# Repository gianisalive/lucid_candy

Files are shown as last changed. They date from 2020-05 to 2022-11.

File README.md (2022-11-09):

# Lucid Candy
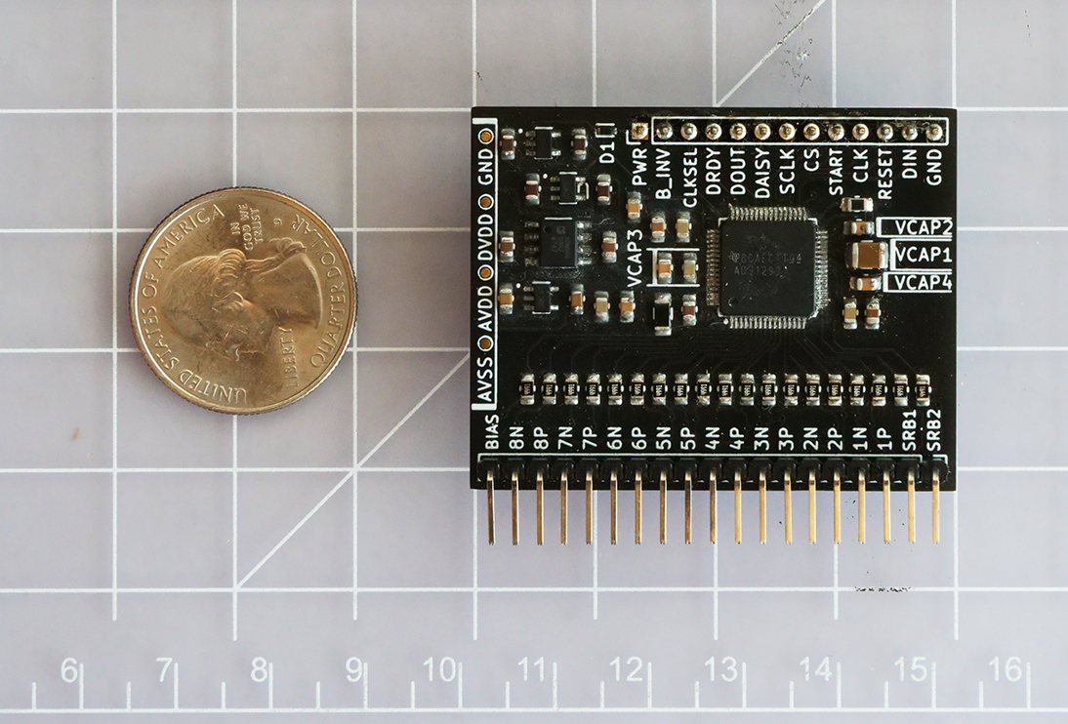
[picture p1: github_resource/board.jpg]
board pic

A bare minimum 8 channel EEG board with TI ads1299 chip. It can be driven with any microcontroller that has 3.3V logic. Multiple boards can be chained together to record with 16 or 24 channels. This repository includes KiCad files and SPI example.

## Disclaimer
It still needs a lot of improvement, professional guidance and review. In no way it's fully tested to perform under clinical setting. Please use basic principles to test and evaluate before using it. All suggestions are highly appreciated: gianisalive@gmail.com

## Who should use it?
No one really should, but if you're a newbie in electronics, software, and neuroscience, and want to learn more by building, then this might be a thing for you. If you're just looking for an affordable EEG, there're better open source ones out there, such as [OpenBCI](https://openbci.com/).

## Files & Locations
|-- lucid_candy  
|---- component_datasheet------important datasheet of the components used for the board  
|---- e_component---------------all the KiCad pcb footprint (from SnapEDA) for the components  
|---- eeg------------------------KiCad design files  
|---- firmware-------------------example of Arduino DUE communicating with the board via SPI  
|---- gerber_zip-----------------same file used to produce the current board with JLCPCB  

## Schematics
The philosophy with current version of the design is to work within TI's recommendation, and choose components with least amount of tolerance/inductance to develope a baseline. In the future, any design improvement can be evaluated/compared to the current design.
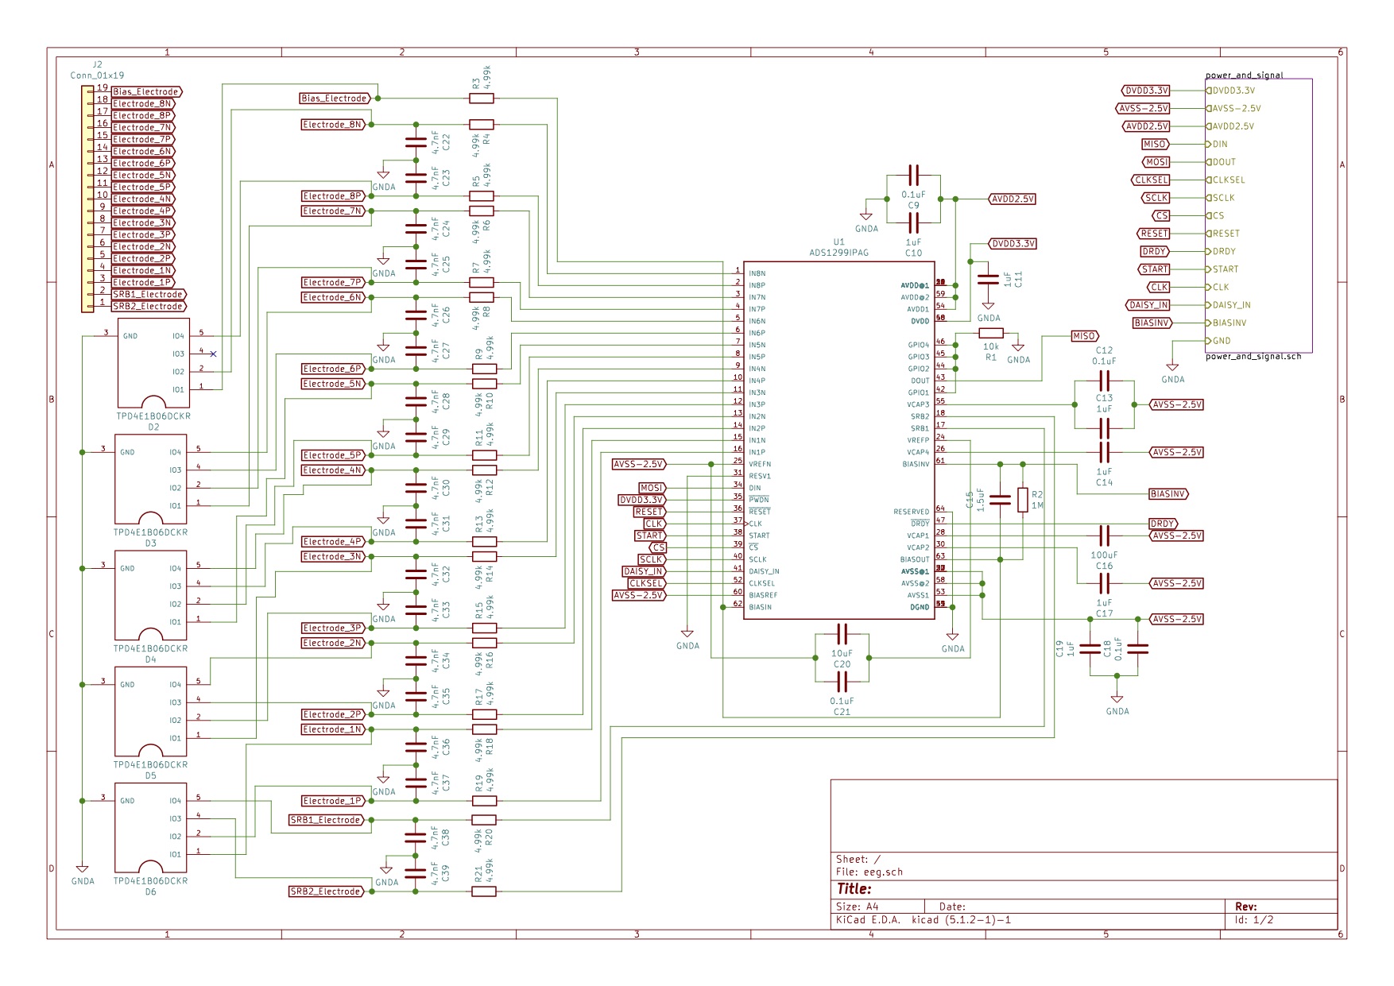
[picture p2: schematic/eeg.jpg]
eeg_schematics

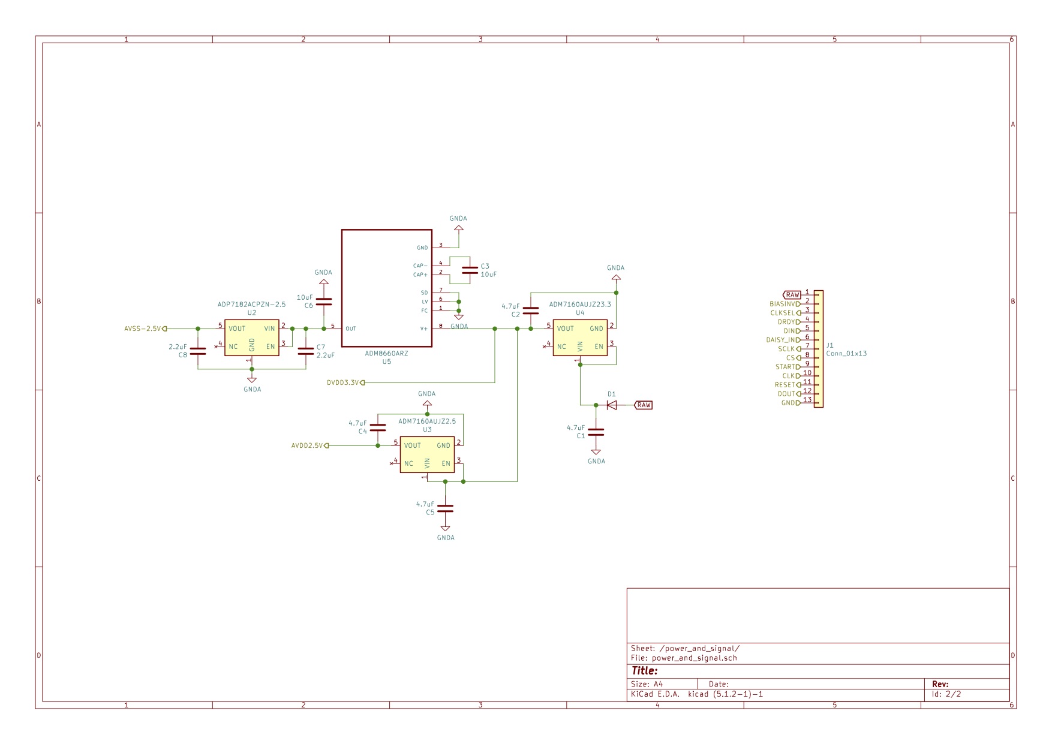
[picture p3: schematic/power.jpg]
power_schematics


## Components
All the component used can be found [here](https://docs.google.com/spreadsheets/d/1N4UGuHjUGolRgQoIL3MemhwEijfZmJlSR52b1LrSyF4/edit?usp=sharing). Some of these are pretty over priced. In most situations, you can probably get away with cheaper parts.

## Programming in a nutshell
**Overview:**  
- Data are transfered via SPI MODE1 with MSB first
- Data are retrieve with no-op command 0x00
- Chip has an internal clock. If BYOO (bring your own oscillator), then connect it to CLK pin, and tie CLKSEL low.  

**Power up sequence:**  
- Set CLKSEL pin high to enable internal oscillator
- Set RESET pin high, and make sure VCAP1 is settled around 1.1V
- Send reset command, and at this point DRDY pin should toggle at around 250Hz
- Send SDATAC (stop data continuous) command
- Set CONFIG1(0x01), CONFIG2(0x02) and CONFIG3(0x03)
- Set CHnSET (single ended, double ended or generate test signal)

**Data conversion:**  
- After sending RDATA or RDATAC command, data is returned on the second rising edge of the DRDY pin
- Initial 3 bytes are status data, and it always starts with 1100. Then it'll transfer 3 bytes of data per channel. An 8 channel board will have 8 * 3 + 3 = 27 bytes of data
- Data are structured in 2's compliment. The MSB is used to determin whether the value is positive or negative
- V = LSB * (2 * 4.5 / 24) / (2 ^ 24) // LSB = decimal value of 3 bytes channel data

## Testing
Fully assembled device with current Arduino firmware is tested with a calibrated Keysight DSOX1204G oscilloscope/function generator.

## Chanllenges
In a nutshell, eliminating noises and extracting the signal is one of the most chanllenging part when it comes to designing the hardware and the software.  
Neurons communcate via electrical signals (Action Potentials). When neurons are ready to send signals to neighboring neurons, they produce about 100 mV spike in less than 3 ms. These signals are further attenuated (reduction in signal strength) by the surrounding anatomical structures. When the electrode receives the signal, it's been attenuated to uV scale. In order to extract the signals, we need to filter out the noise with minimal distortion to the signal. There're few methods suggest that're yet to be implemented, such as bandpass filter, CleanLine and infinite impulse response.

## Miscellaneous
Some silly questions I asked:
 - [voltage offset](https://e2e.ti.com/support/data-converters/f/73/p/912858/3374371#3374371)

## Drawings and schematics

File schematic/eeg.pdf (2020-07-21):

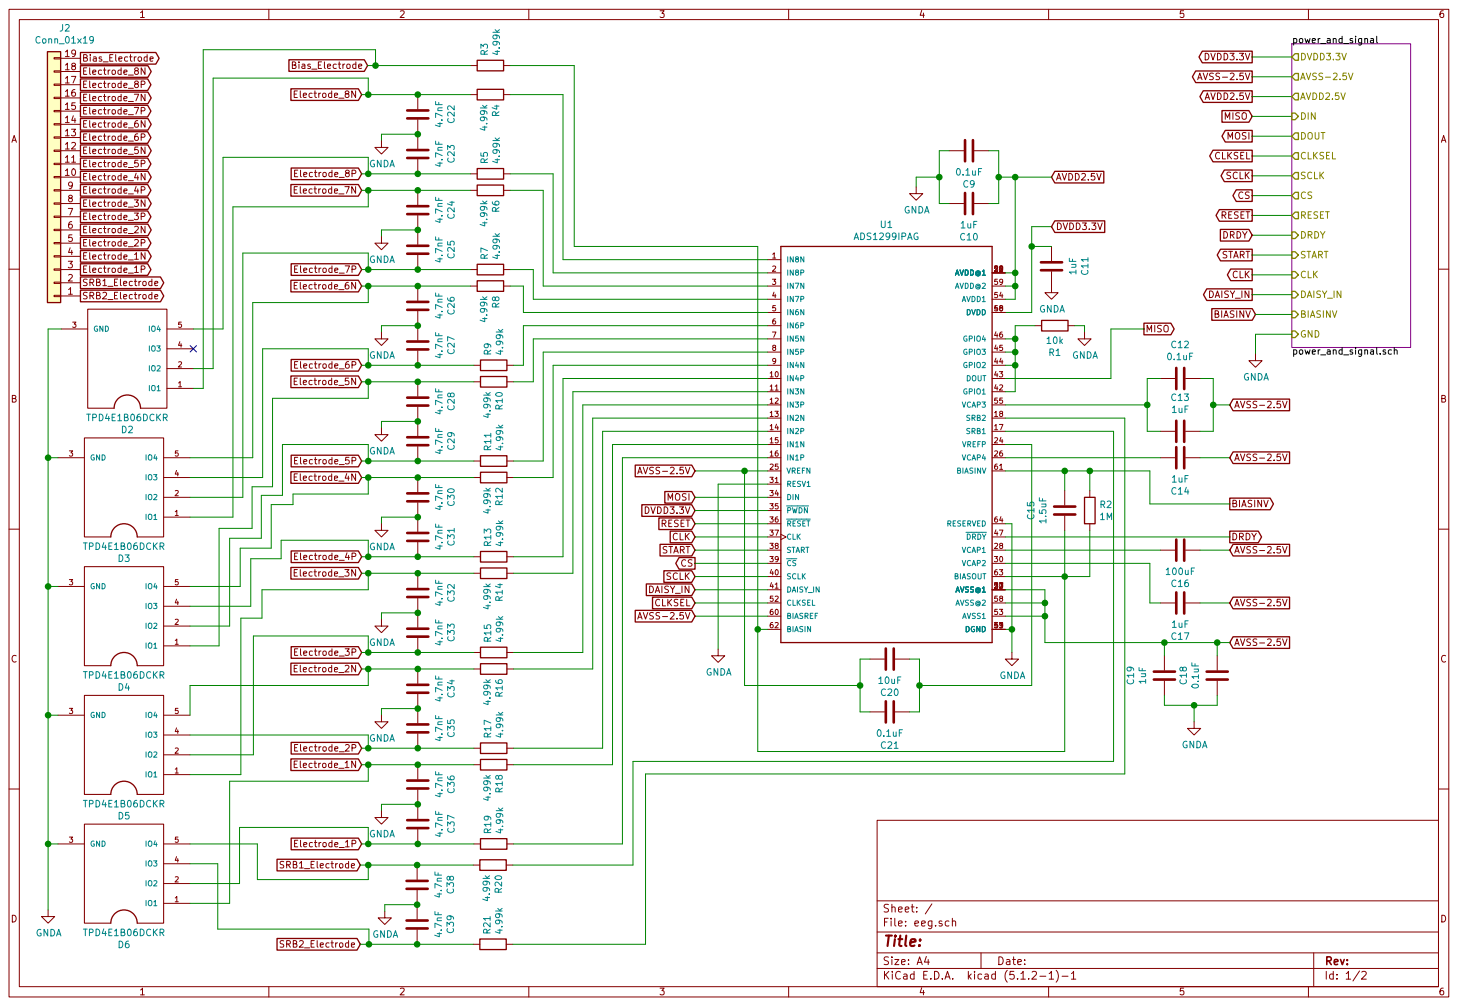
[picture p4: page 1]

IN5N 7
IN5P 8
IN4N 9
IN4P 10
IN3N 11
IN3P 12
IN2N 13

File: eeg.sch Sheet: /

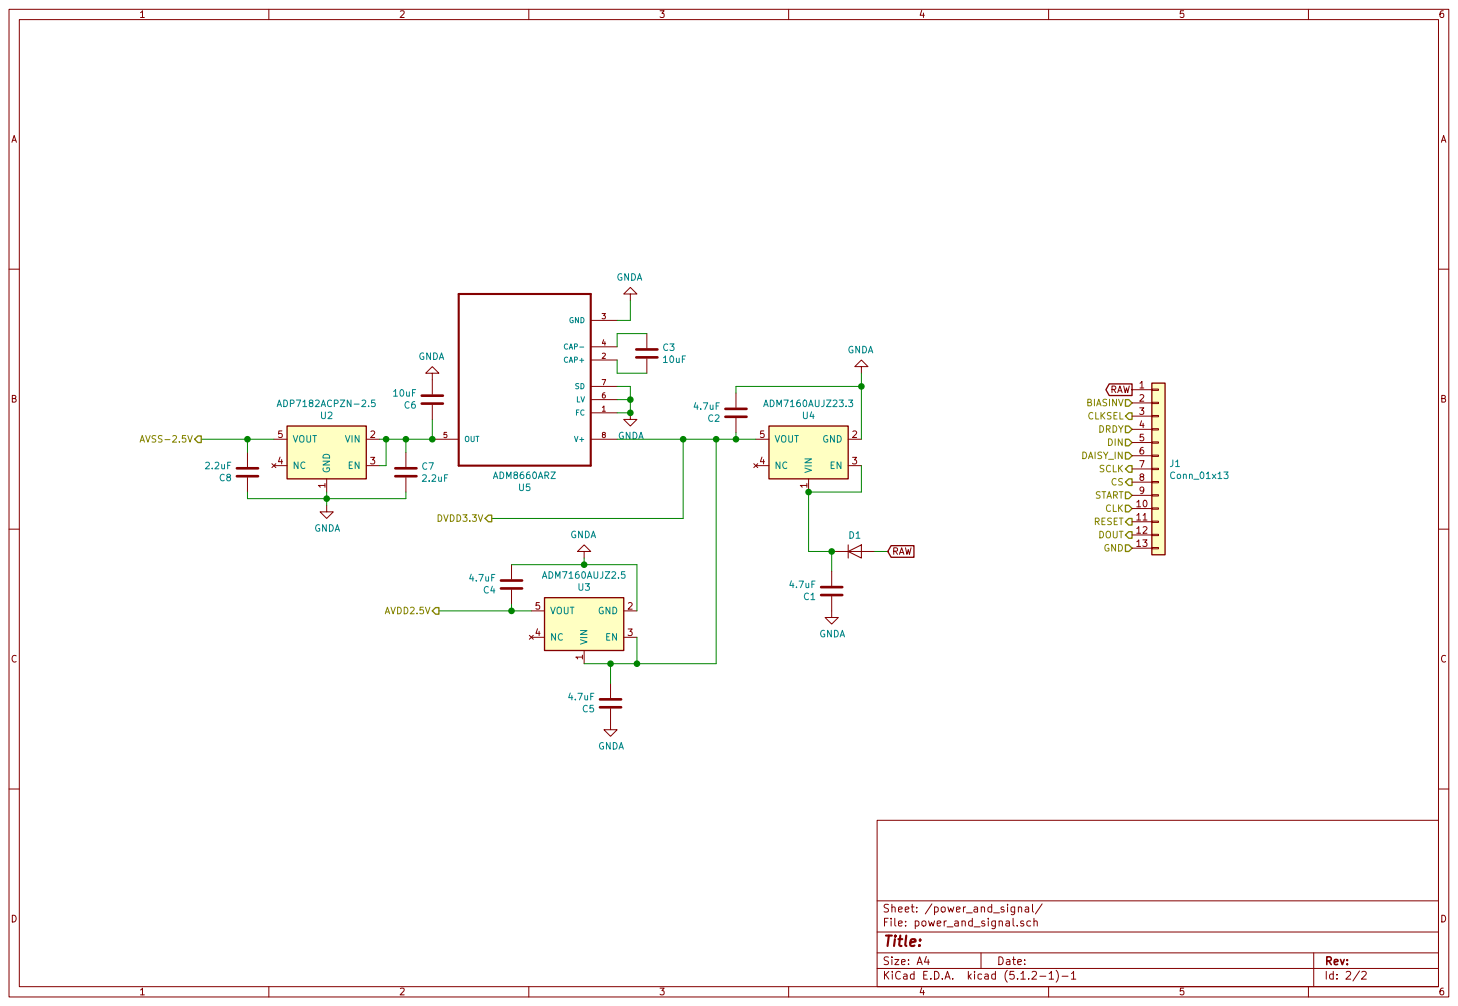
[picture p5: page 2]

1 VIN 2 EN 3 NC 4 VOUT 5 U2 ADP7182ACPZN-2.5 GNDA C7 C8 2.2uF

1 GND 2 EN 3 NC 4 VOUT 5 U4 ADM7160AUJZ23.3 C2

1 GND 2 EN 3 NC 4 VOUT 5 U3 ADM7160AUJZ2.5 C4

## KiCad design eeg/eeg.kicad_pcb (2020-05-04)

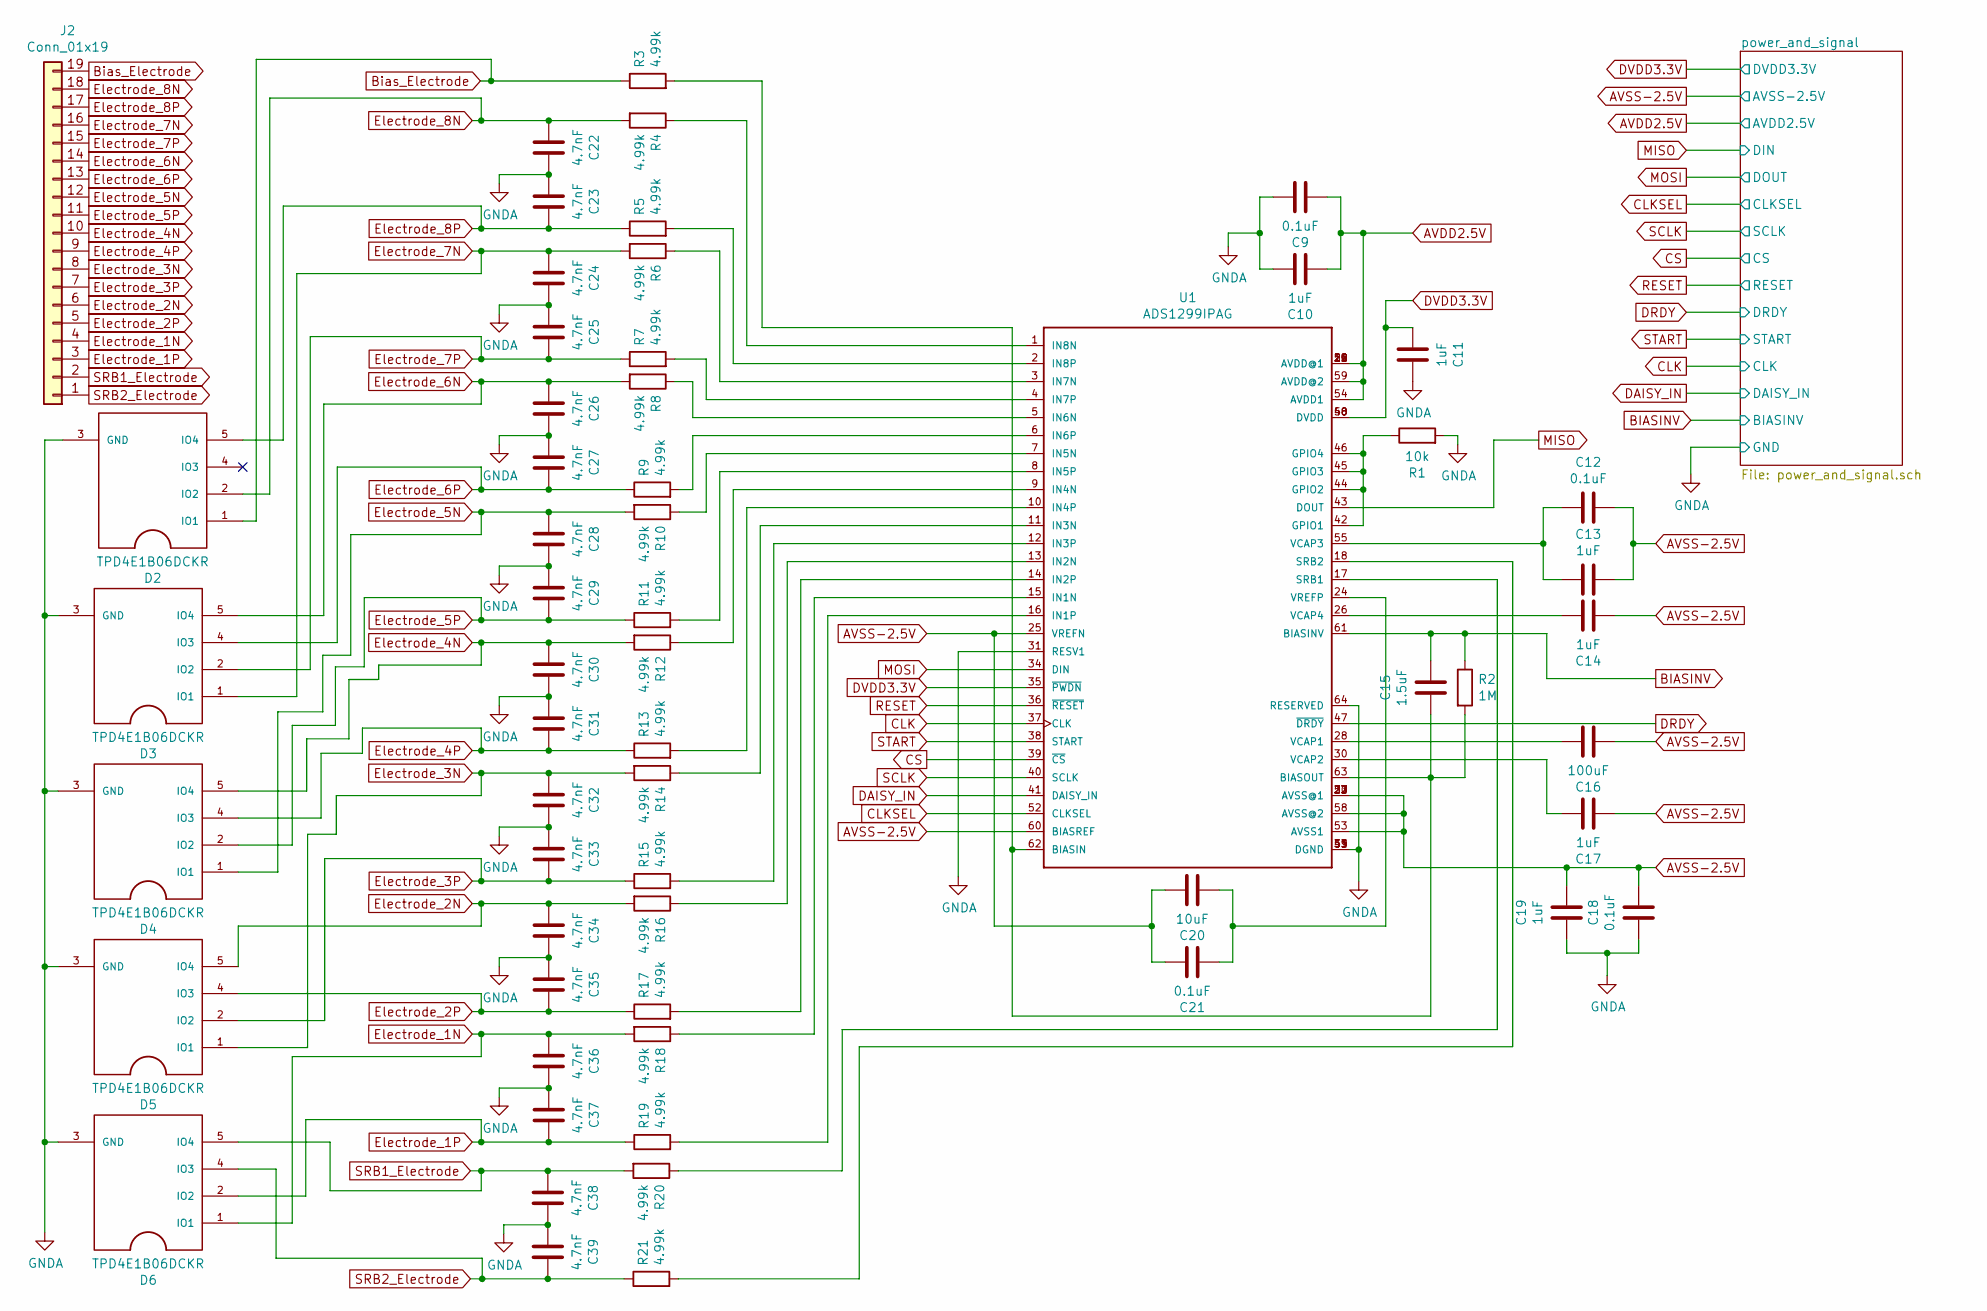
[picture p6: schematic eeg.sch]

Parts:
C9, C12, C18, C21: 0.1uF; C_0805_2012Metric_Pad1.15x1.40mm_HandSolder
C10, C11, C13, C14, C17, C19: 1uF; C_0805_2012Metric_Pad1.15x1.40mm_HandSolder
C15: 1.5uF; C_0805_2012Metric_Pad1.15x1.40mm_HandSolder
C16: 100uF; C_1210_3225Metric_Pad1.42x2.65mm_HandSolder
C20: 10uF; C_0805_2012Metric_Pad1.15x1.40mm_HandSolder
C22, C23, C24, C25, C26, C27, C28, C29, C30, C31, C32, C33, C34, C35, C36, C37, C38, C39: 4.7nF; C_0805_2012Metric_Pad1.15x1.40mm_HandSolder
D2, D3, D4, D5, D6: TPD4E1B06DCKR
J2: Conn_01x19; PinHeader_1x19_P2.54mm_Vertical
R1: 10k; R_0805_2012Metric_Pad1.15x1.40mm_HandSolder
R2: 1M; R_1206_3216Metric_Pad1.42x1.75mm_HandSolder
R3, R4, R5, R6, R7, R8, R9, R10, R11, R12, R13, R14, R15, R16, R17, R18, R19, R20, R21: 4.99k; R_0805_2012Metric_Pad1.15x1.40mm_HandSolder
U1: ADS1299IPAG

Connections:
AVDD2.5V: C9.1, C10.1, U1.19 (AVDD@1), U1.21 (AVDD@1), U1.22 (AVDD@1), U1.54 (AVDD1), U1.56 (AVDD@1), U1.59 (AVDD@2); also elsewhere on the board
AVSS-2.5V: C12.2, C13.2, C14.1, C16.1, C17.1, C18.2, C19.2, C20.2, C21.2, U1.20 (AVSS@1), U1.23 (AVSS@1), U1.25 (VREFN), U1.32 (AVSS@1), U1.53 (AVSS1), U1.57 (AVSS@1), U1.58 (AVSS@2), U1.60 (BIASREF); also elsewhere on the board
BIASINV: C15.2, R2.1, U1.61 (BIASINV); also elsewhere on the board
Bias_Electrode: D2.1 (IO1), J2.19, R3.1
CLK: U1.37 (CLK); also elsewhere on the board
CLKSEL: U1.52 (CLKSEL); also elsewhere on the board
CS: U1.39 (~CS~); also elsewhere on the board
DAISY_IN: U1.41 (DAISY_IN); also elsewhere on the board
DRDY: U1.47 (~DRDY~); also elsewhere on the board
DVDD3.3V: C11.1, U1.35 (~PWDN~), U1.48 (DVDD), U1.50 (DVDD); also elsewhere on the board
Electrode_1N: C36.1, D6.1 (IO1), J2.4, R18.2
Electrode_1P: C37.2, D6.2 (IO2), J2.3, R19.1
Electrode_2N: C34.1, D5.5 (IO4), J2.6, R16.2
Electrode_2P: C35.2, D5.4 (IO3), J2.5, R17.1
Electrode_3N: C32.1, D5.1 (IO1), J2.8, R14.2
Electrode_3P: C33.2, D5.2 (IO2), J2.7, R15.1
Electrode_4N: C30.1, D4.5 (IO4), J2.10, R12.2
Electrode_4P: C31.2, D4.4 (IO3), J2.9, R13.1
Electrode_5N: C28.1, D4.1 (IO1), J2.12, R10.2
Electrode_5P: C29.2, D4.2 (IO2), J2.11, R11.1
Electrode_6N: C26.1, D3.5 (IO4), J2.14, R8.2
Electrode_6P: C27.2, D3.4 (IO3), J2.13, R9.1
Electrode_7N: C24.1, D3.1 (IO1), J2.16, R6.2
Electrode_7P: C25.2, D3.2 (IO2), J2.15, R7.1
Electrode_8N: C22.1, D2.2 (IO2), J2.18, R4.2
Electrode_8P: C23.2, D2.5 (IO4), J2.17, R5.1
GNDA: C9.2, C10.2, C11.2, C18.1, C19.1, C22.2, C23.1, C24.2, C25.1, C26.2, C27.1, C28.2, C29.1, C30.2, C31.1, C32.2, C33.1, C34.2, C35.1, C36.2, C37.1, C38.2, C39.1, D2.3 (GND), D3.3 (GND), D4.3 (GND), D5.3 (GND), D6.3 (GND), R1.2, U1.31 (RESV1), U1.33 (DGND), U1.49 (DGND), U1.51 (DGND), U1.64 (RESERVED); also elsewhere on the board
MISO: U1.43 (DOUT); also elsewhere on the board
MOSI: U1.34 (DIN); also elsewhere on the board
unnamed: C12.1, C13.1, U1.55 (VCAP3)
unnamed: C14.2, U1.26 (VCAP4)
unnamed: C15.1, R2.2, R3.2, U1.62 (BIASIN), U1.63 (BIASOUT)
unnamed: C16.2, U1.28 (VCAP1)
unnamed: C17.2, U1.30 (VCAP2)
unnamed: C20.1, C21.1, U1.24 (VREFP)
unnamed: R1.1, U1.42 (GPIO1), U1.44 (GPIO2), U1.45 (GPIO3), U1.46 (GPIO4)
unnamed: R4.1, U1.1 (IN8N)
unnamed: R5.2, U1.2 (IN8P)
unnamed: R6.1, U1.3 (IN7N)
unnamed: R7.2, U1.4 (IN7P)
unnamed: R8.1, U1.5 (IN6N)
unnamed: R9.2, U1.6 (IN6P)
unnamed: R10.1, U1.7 (IN5N)
unnamed: R11.2, U1.8 (IN5P)
unnamed: R12.1, U1.9 (IN4N)
unnamed: R13.2, U1.10 (IN4P)
unnamed: R14.1, U1.11 (IN3N)
unnamed: R15.2, U1.12 (IN3P)
unnamed: R16.1, U1.13 (IN2N)
unnamed: R17.2, U1.14 (IN2P)
unnamed: R18.1, U1.15 (IN1N)
unnamed: R19.2, U1.16 (IN1P)
unnamed: R20.1, U1.17 (SRB1)
unnamed: R21.2, U1.18 (SRB2)
RESET: U1.36 (~RESET~); also elsewhere on the board
SCLK: U1.40 (SCLK); also elsewhere on the board
SRB1_Electrode: C38.1, D6.5 (IO4), J2.2, R20.2
SRB2_Electrode: C39.2, D6.4 (IO3), J2.1, R21.1
START: U1.38 (START); also elsewhere on the board

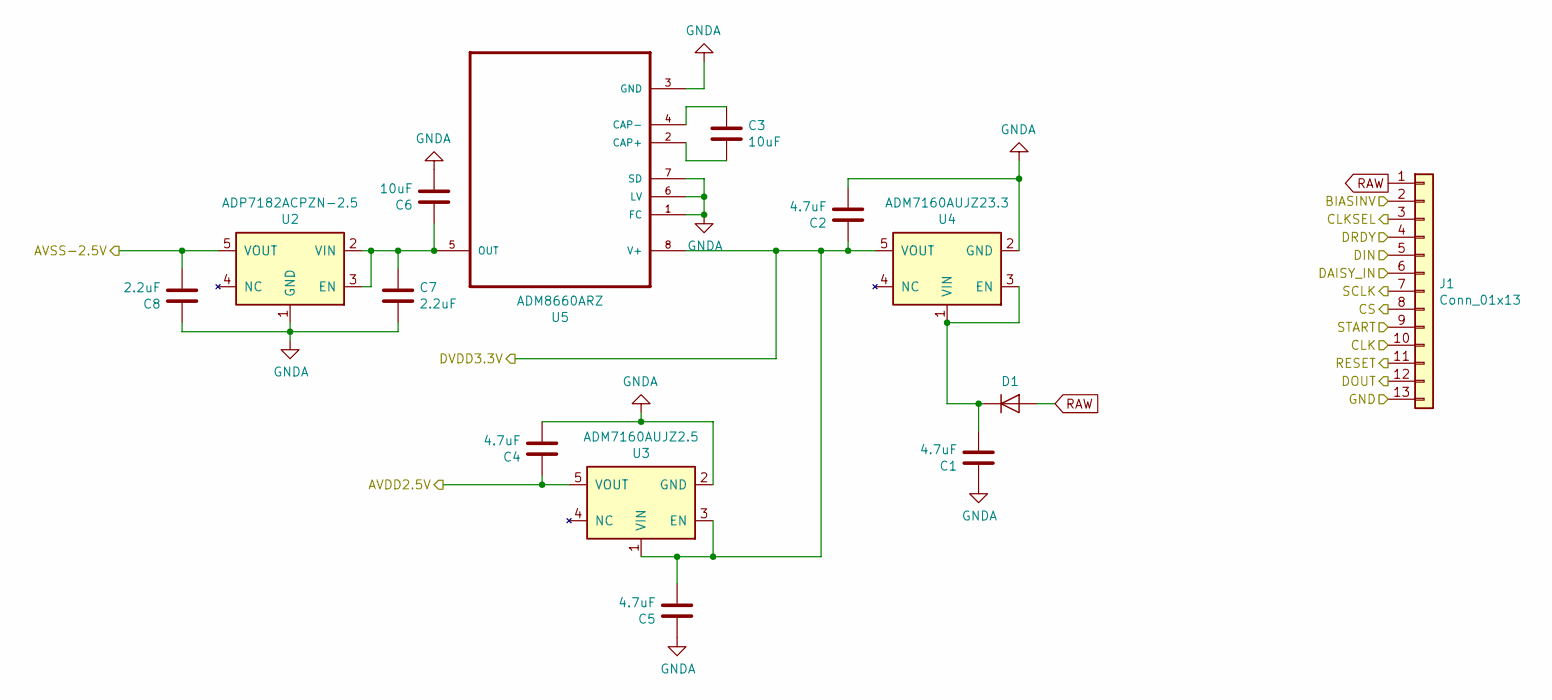
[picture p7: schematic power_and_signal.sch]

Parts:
C1, C2, C4, C5: 4.7uF; C_0805_2012Metric_Pad1.15x1.40mm_HandSolder
C3, C6: 10uF; C_0805_2012Metric_Pad1.15x1.40mm_HandSolder
C7, C8: 2.2uF; C_0805_2012Metric_Pad1.15x1.40mm_HandSolder
D1: D; D_SOD-523
J1: Conn_01x13; PinHeader_1x13_P2.54mm_Vertical
U2: ADP7182ACPZN-2.5; Analog_TSOT-5
U3: ADM7160AUJZ2.5; Analog_TSOT-5
U4: ADM7160AUJZ23.3; Analog_TSOT-5
U5: ADM8660ARZ

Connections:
AVDD2.5V: C4.1, U3.5 (VOUT); also elsewhere on the board
AVSS-2.5V: C8.2, U2.5 (VOUT); also elsewhere on the board
BIASINV: J1.2; also elsewhere on the board
CLK: J1.10; also elsewhere on the board
CLKSEL: J1.3; also elsewhere on the board
CS: J1.8; also elsewhere on the board
DAISY_IN: J1.6; also elsewhere on the board
DRDY: J1.4; also elsewhere on the board
DVDD3.3V: C2.1, C5.2, U3.1 (VIN), U3.3 (EN), U4.5 (VOUT), U5.8 (V+); also elsewhere on the board
GNDA: C1.1, C2.2, C4.2, C5.1, C6.2, C7.2, C8.1, J1.13, U2.1 (GND), U3.2 (GND), U4.2 (GND), U5.1 (FC), U5.3 (GND), U5.6 (LV), U5.7 (SD); also elsewhere on the board
MISO: J1.5; also elsewhere on the board
MOSI: J1.12; also elsewhere on the board
unnamed: C1.2, D1.1 (K), U4.1 (VIN), U4.3 (EN)
unnamed: C3.1, U5.4 (CAP-)
unnamed: C3.2, U5.2 (CAP+)
unnamed: C6.1, C7.1, U2.2 (VIN), U2.3 (EN), U5.5 (OUT)
RAW: D1.2 (A), J1.1
RESET: J1.11; also elsewhere on the board
SCLK: J1.7; also elsewhere on the board
START: J1.9; also elsewhere on the board

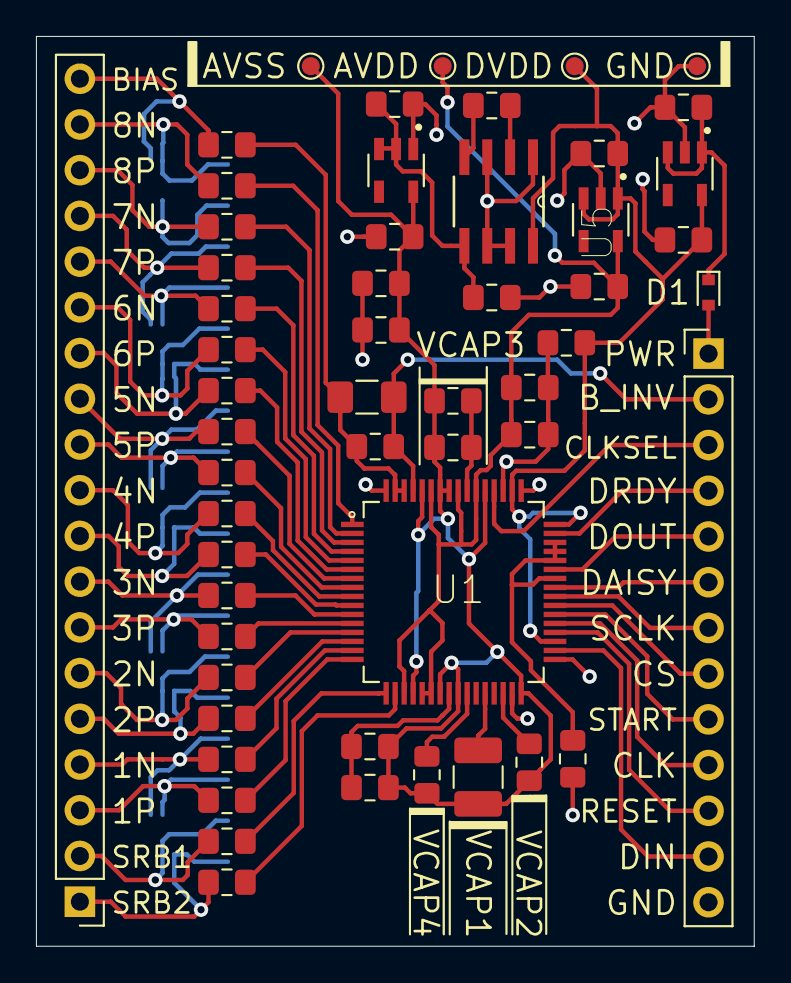
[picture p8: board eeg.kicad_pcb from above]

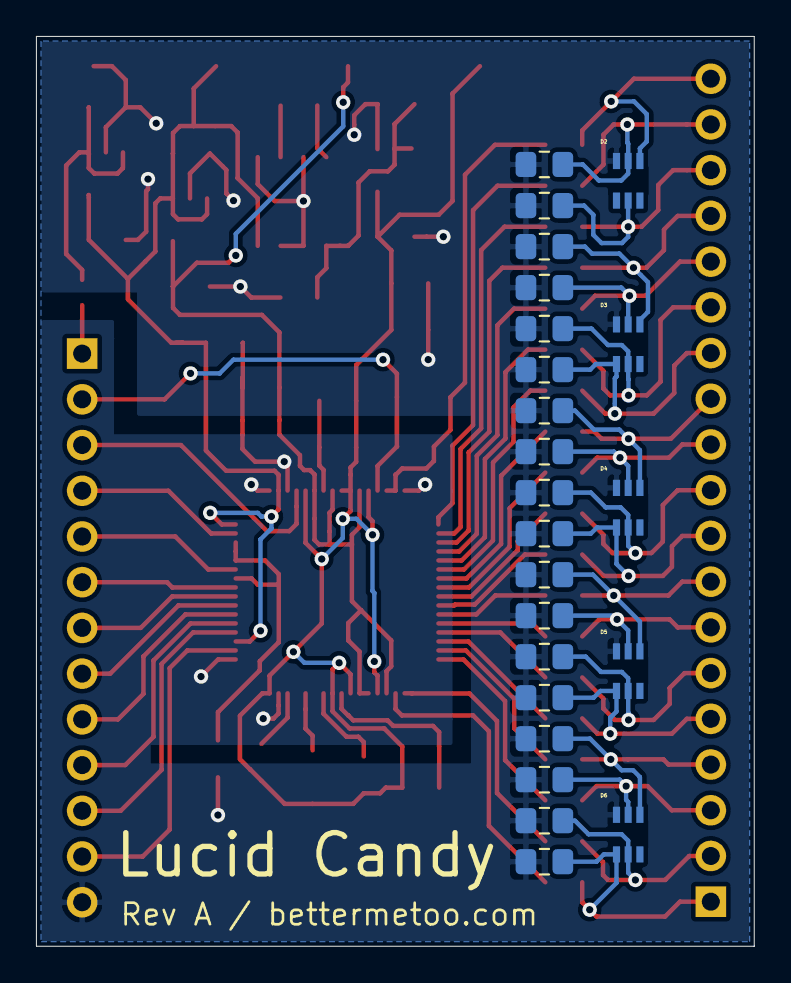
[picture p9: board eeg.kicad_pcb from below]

Board: 2 copper layers, 39.9 x 50.5 mm, 77 parts (23 on the bottom side), 64 nets.

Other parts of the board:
AVDD: TestPoint_Pad_D1.0mm
AVSS: TestPoint_Pad_D1.0mm
DVDD: TestPoint_Pad_D1.0mm
GND: TestPoint_Pad_D1.0mm

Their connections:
AVDD2.5V: AVDD.1; also elsewhere on the board
AVSS-2.5V: AVSS.1; also elsewhere on the board
DVDD3.3V: DVDD.1; also elsewhere on the board
GNDA: GND.1; also elsewhere on the board

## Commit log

2020-05-14 get device ID, enable internal oscillator
2020-05-19 print device ID and read full byte of data
2020-06-18 adjust gain setting and improve power up sequence timing
2020-06-21 read data at 250hz
2020-06-23 send device data via serial port upon request
2020-07-21 include device schematic
2020-08-12 higher sample rate
